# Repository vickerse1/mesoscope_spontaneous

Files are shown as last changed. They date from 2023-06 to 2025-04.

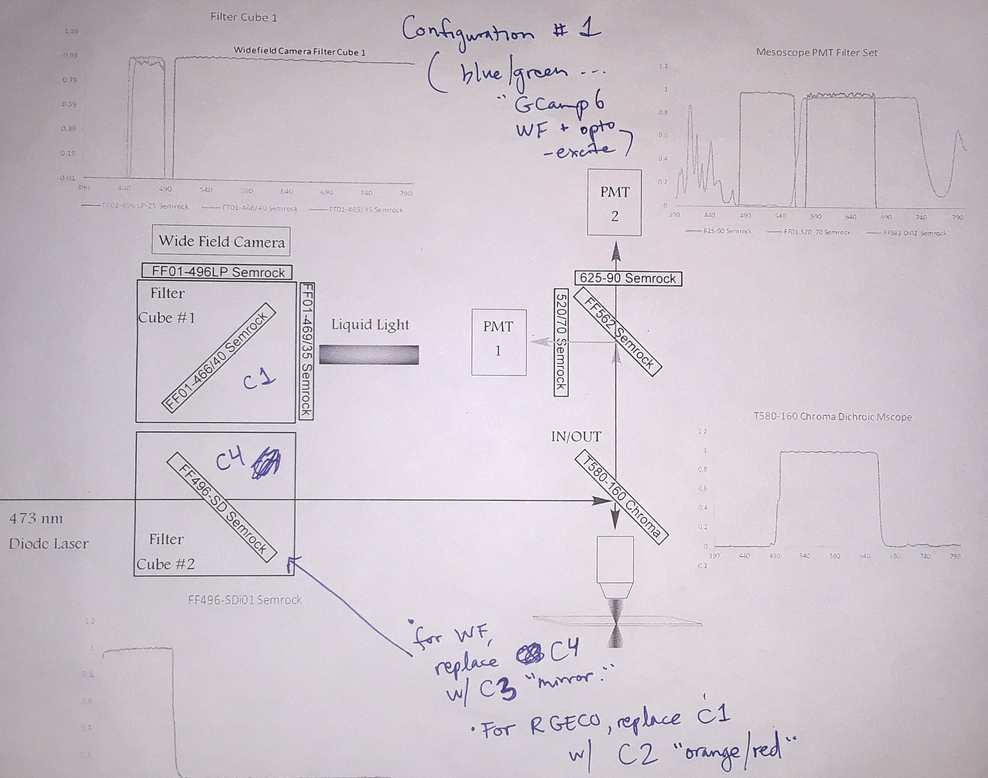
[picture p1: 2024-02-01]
mesoscope_filterCube_schematic_dual_opto_Jan0320.jpg

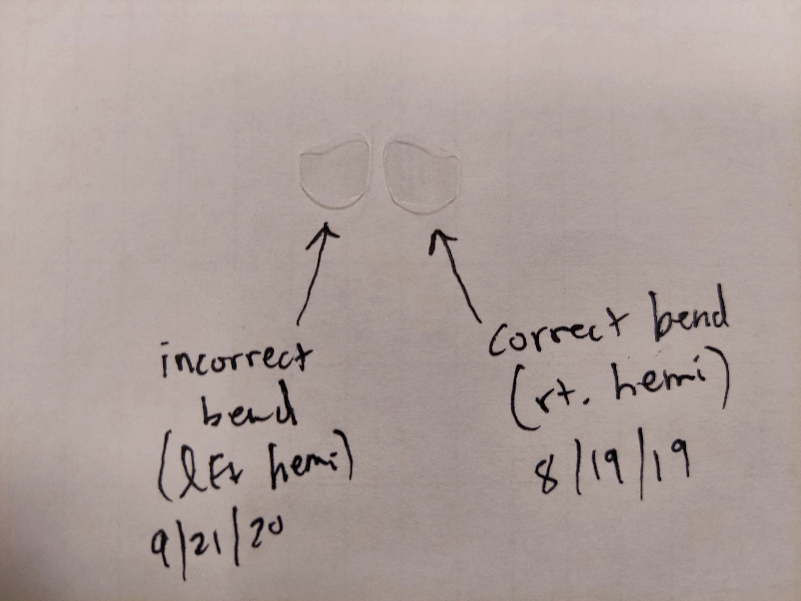
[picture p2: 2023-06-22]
cranial_windows/side_mount/side_mount_chirality_image_1.jpg

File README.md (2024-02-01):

# mesoscope_spontaneous

These files are associated with the following paper (PLEASE CITE - now online both at bioRxiv and as a reviewed preprint at eLife):

bioRxiv:

doi: [https://doi.org/10.1101/2023.10.19.563159]

eLife reviewed preprint:

[https://doi.org/10.7554/eLife.94167]

Publicly available datasets at FigShare+:

[https://doi.org/10.25452/figshare.plus.c.7052513]

"Pan-cortical 2-photon mesoscopic imaging and neurobehavioral alignment in awake, behaving mice"

Evan D. Vickers1 and David A. McCormick1,2,3

1Institute of Neuroscience, Eugene, OR. 2Professor, Department of Biology. 3Director, Institute of Neuroscience

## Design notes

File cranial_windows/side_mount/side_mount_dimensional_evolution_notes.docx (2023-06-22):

Dec2018: 10.46 mm length (ML), 9.6 mm width (AP), 10 mm radius

Aug2019: 9.8 mm length (ML), 8.8 mm width (AP), 10 and 9 mm radius (50pc/50pc)

Jul18 2020: 9.6 mm length (ML), 7.97 mm width (AP)

Jul20 2020: 8.9 mm length (ML), 7.62 mm width (AP)

Major problems:

AP too long to fit in headpost just right of midline.

Glass comes up dorsally from surface of brain just left of midline.

Glass does not drop ventrally enough over ventral A1

Solutions:

Shorten AP dimension.

Shorten ML dimension.

Decrease bend radius from 10 to 9 mm.

Concerns with new smaller glass designs: too small at AM edge to get all of M2, too small at PM edge to get all of V1?

-e

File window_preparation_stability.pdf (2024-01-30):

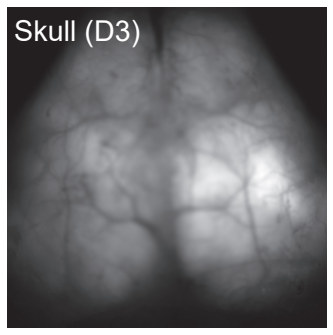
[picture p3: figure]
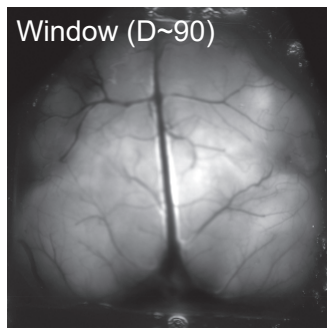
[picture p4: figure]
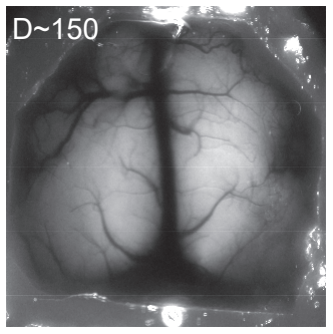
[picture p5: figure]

a | Skull (D3) | Window (D~90) | D~150

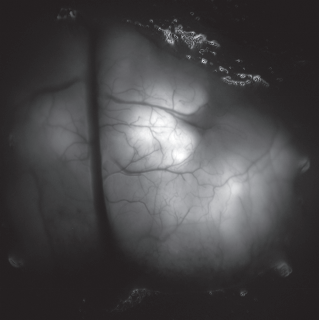
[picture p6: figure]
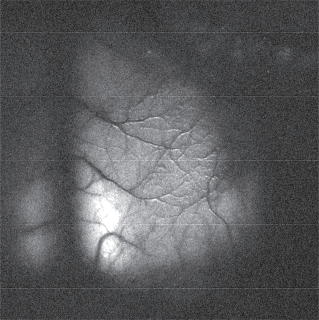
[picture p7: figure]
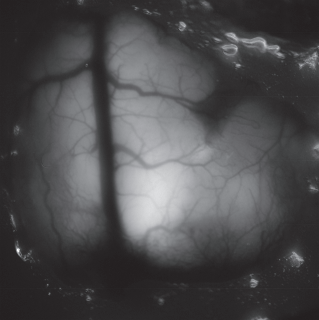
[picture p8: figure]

b

## dorsal mount

ex.

## side mount

ex.

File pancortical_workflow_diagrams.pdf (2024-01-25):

a)

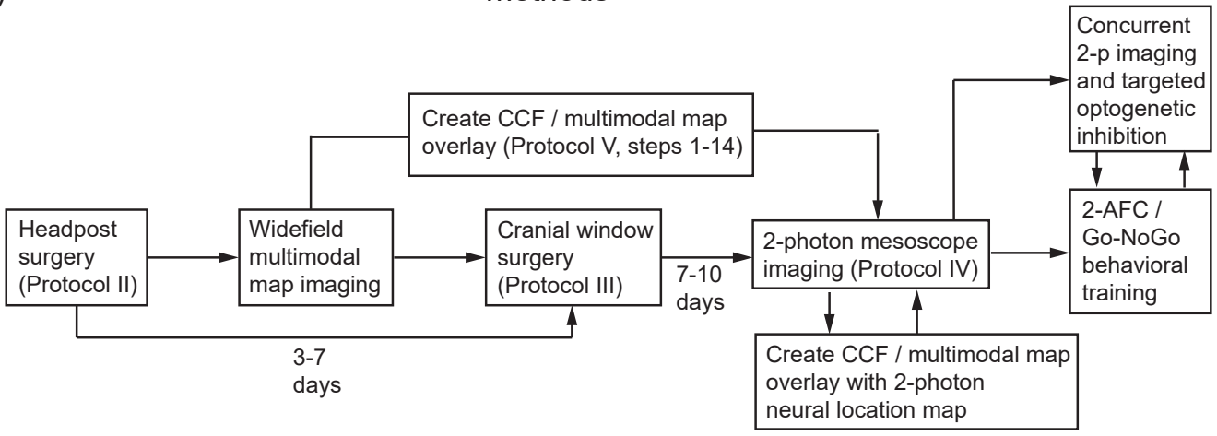
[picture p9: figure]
Headpost surgery (Protocol II); Widefield multimodal map imaging; Cranial window surgery (Protocol III); 3-7 days; 7-10 days; 2-photon mesoscope imaging (Protocol IV); Create CCF / multimodal map overlay (Protocol V, steps 1-14); Create CCF / multimodal map overlay with 2-photon neural location map; Concurrent 2-p imaging and targeted optogenetic inhibition; 2-AFC / Go-NoGo behavioral training

b)

d)

## methods

## widefield data acquisition

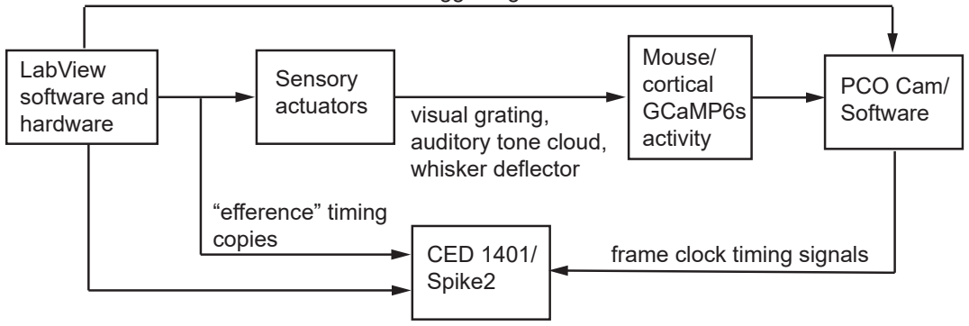
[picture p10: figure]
Sensory actuators; LabView software and hardware; CED 1401/ Spike2; PCO Cam/ Software; Mouse/ cortical GCaMP6s activity; visual grating, auditory tone cloud, whisker deflector; “efference” timing copies; frame clock timing signals
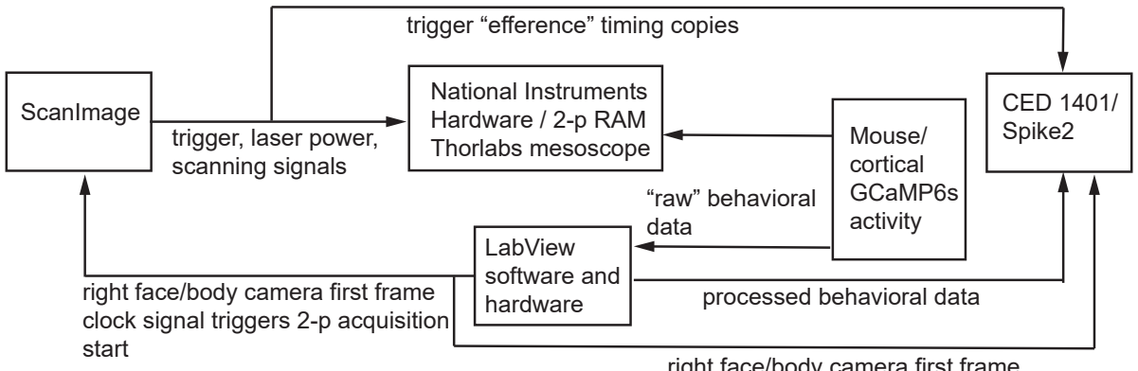
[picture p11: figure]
ScanImage; National Instruments Hardware / 2-p RAM Thorlabs mesoscope; CED 1401/ Spike2; LabView software and hardware; Mouse/ cortical GCaMP6s activity; trigger “efference” timing copies; trigger, laser power, scanning signals; right face/body camera first frame clock signal triggers 2-p acquisition start; processed behavioral data; “raw” behavioral data

## analysis

## c) 2-photon data acquisition

trigger signals

right face/body camera first frame clock signal triggers Spike2 start

Multimodal mapping/
CCF alignment
(Matlab)

Suite2p analysis
(Python)

Jupyter notebooks
mesoscope “preprocessing”
(Python)

Post-processing:
community structures
and functional connectivity (Python)

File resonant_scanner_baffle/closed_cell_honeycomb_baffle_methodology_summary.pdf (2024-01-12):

## SUMMARY OF THE INVENTION

To study the neuronal networks in behaving animals, the University of Oregon Institute of Neuroscience (ION) acquired a Thorlabs 2-photon mesoscope. This mesoscope allows for the recording of activity of over 10,000 neurons simultaneously at single-cell resolution with an acquisition rate of ~3 Hz over much of one hemisphere of the cerebral cortex of a mouse while they perform complex tasks in real-time. These tasks can involve seeing, hearing, smelling, movement, etc., even in a virtual environment.

During the auditory tests, the inventors detected unwanted high-frequency noise from the mesoscope. This noise is also detected by the mice performing auditory tasks and interferes with the data collection task being performed. Using a microphone and an oscilloscope, the inventors discovered the source of the noise to be the resonant scanners and the tubes that connect the light paths.

The inventors discovered a solution to reduce the noise level of the high-frequency sound, making use of 3D-Printers and software that enable complex designing and manufacturing of devices for optimizing scientific instrumentations. The inventors 3D-Scanned and designed a baffle having both solid and closed-cell honeycomb lattice. After installing the baffle, the high-frequency (12.5 kHz) noise went from 60 dB without the baffle down to an average of 10 dB with the baffle installed. The mice are not able to hear the high-frequency sound if the noise is below 16 dB at this sound frequency, based on published, species-specific auditory brainstem response threshold curves. Therefore, adding the baffle resulted in the mice not being able to hear the sound and also made a significant improvement in the data collection for both generic experiments where the mouse is awake and will experience stress as a result of the sound, and auditory-task-based research where precise control over the auditory environment is critical.

The sound pressure level was measured with a Bruel and Kjaer 4938 1/4" pressure-field microphone (see attached) calibrated with a Bruel and Kjaer Type 4231 Sound Calibrator, with the microphone signal amplified through a Bruel and Kjaer 1708 sound conditioner.

The sound measurements were recorded in fast fourier transform mode (FFT) on a Tektronix TDS 1002 oscilloscope. Each division on the oscilloscope display corresponded to an explicit, calibrated sound pressure level increment in decibels (dB). The output from the sound conditioner to the oscilloscope was sent by BNC cable.

A Creaform HandyScan Black Elite 3D-Scanner was used to create a digital CAD of the existing setup of the Thorlabs Mesoscope. Live capture of the scan data was performed using VX Elements software and the same software was used to convert the live scan to a CAD file of .STL (stereolithography) file format. Using the scanned CAD as a reference, the team designed a baffle to custom fit onto the mesoscope resonant scanner and tubes using Autodesk Fusion-360 software. After designing the baffles, the CAD file of the designed baffle was imported into Materialise Magics software and the lattice design having solid walls followed by honeycomb latticing was designed using this software. The latticed files were saved in .STL file format. In addition, using Materialise Magics, a manual fixing operation was done on certain regions of the imported CAD which had unwanted noise shells, planar holes, overlapping triangles – all of which were fixed to ensure a high quality CAD file is produced for 3D-Printing.

The final baffle design included mediums of varying densities from solid walls and honeycomb latticing to 3D-Print in Nylon. The baffle was printed using Powder Bed Fusion technology using Formlabs Fuse machine, where Nylon material is sintered layer-by-layer to create a 3D-object. The design intent of the honeycomb lattice was to allow for nylon material to be enclosed inside the closed cells during the printing process. The inventors added a clearance design between the baffle and the resonant scanning components to allow for the fitment of polyurethane foam. This created a baffle where high-frequency sound waves had to penetrate through foam, solid nylon wall, enclosed nylon powder inside the honeycomb followed by a second solid wall.

The adhesive back foam used for the baffle was Polyurethane foam 1/8 inches thick and medium soft with 3/16 inch extra soft foam. The foam was cut to shape using a laser cutter to adhere to the 3D-Printed components. High-frequency noise data were collected with a microphone and an oscilloscope. The microphone was fixtured in the general area of the location where the mice would perform auditory tasks.

The baffle is a first-of-its-kind attachment to the Thorlabs Mesoscope (US Pats. 10901194 and 10295811, incorporated herein by reference) and is not commercially available. Since 3D printing allows for mass customization, this baffle can be adapted for any resonant scanning microscopes on the market. This will reduce unwanted noise levels from the experiments yielding to better experimental results for auditory research and also allow for a safer environment for users since the high-frequency noise can be detected by researchers and users of such devices.

The target goal was to lower the noise level to below 16 dB when performing auditory tasks on mice. The results indicate that the 12.5 kHz noise went from 60 dB without the baffle down to an average of 10 dB with the baffle installed.

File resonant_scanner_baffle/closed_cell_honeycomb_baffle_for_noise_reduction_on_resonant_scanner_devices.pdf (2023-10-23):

Closed-cell honeycomb baffle for high-frequency noise reduction on Resonant Scanning devices

Supplementary Document

3D-Scanning

The 3D-Scanning is performed to ensure a) an accurate digital representation of the setup is captured for reverse engineering a custom-fit baffle around the components. b) to perform a virtual fitment check to ensure the designed baffle fits the existing components.

The software used to capture scanned point cloud data is Creaform VX Elements and the file is aligned to coordinate planes using Materialise Magics.

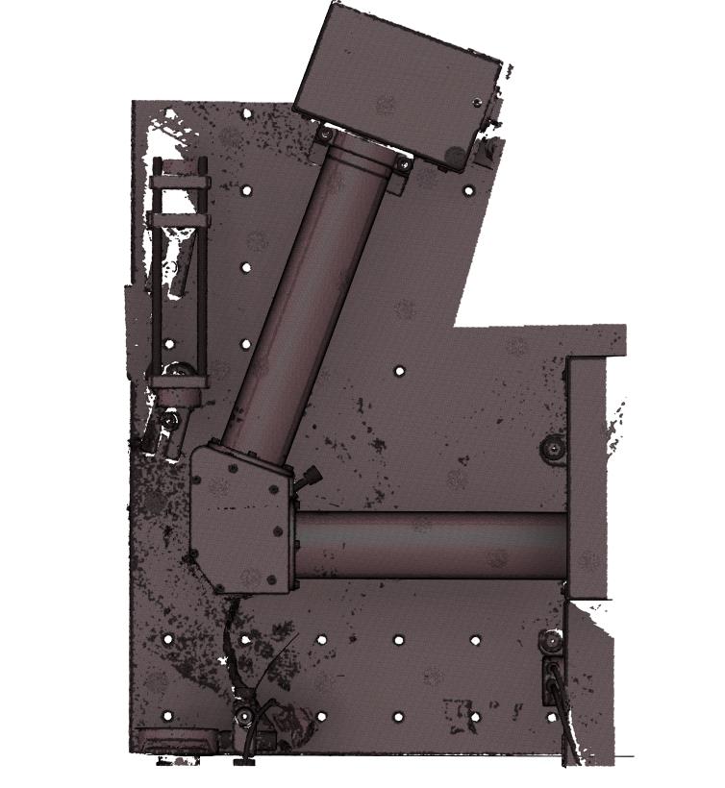
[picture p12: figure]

Reverse Engineering

Using the 3D-scan file, a custom baffle enclosure is designed using Autodesk Fusion-360. The components are designed to be produced in seven individual pieces for a) easy disassembling for technicians and b) constraints set forth by the limited printable build area by the 3D-Printer. This design consisted of solid walls that will be later used to create latticing on the inside and also contains an offset for an after-market polyurethane foam to compress. The design has custom screws and plugs for adjustment of a calibration screw fitted in the resonant tubes.

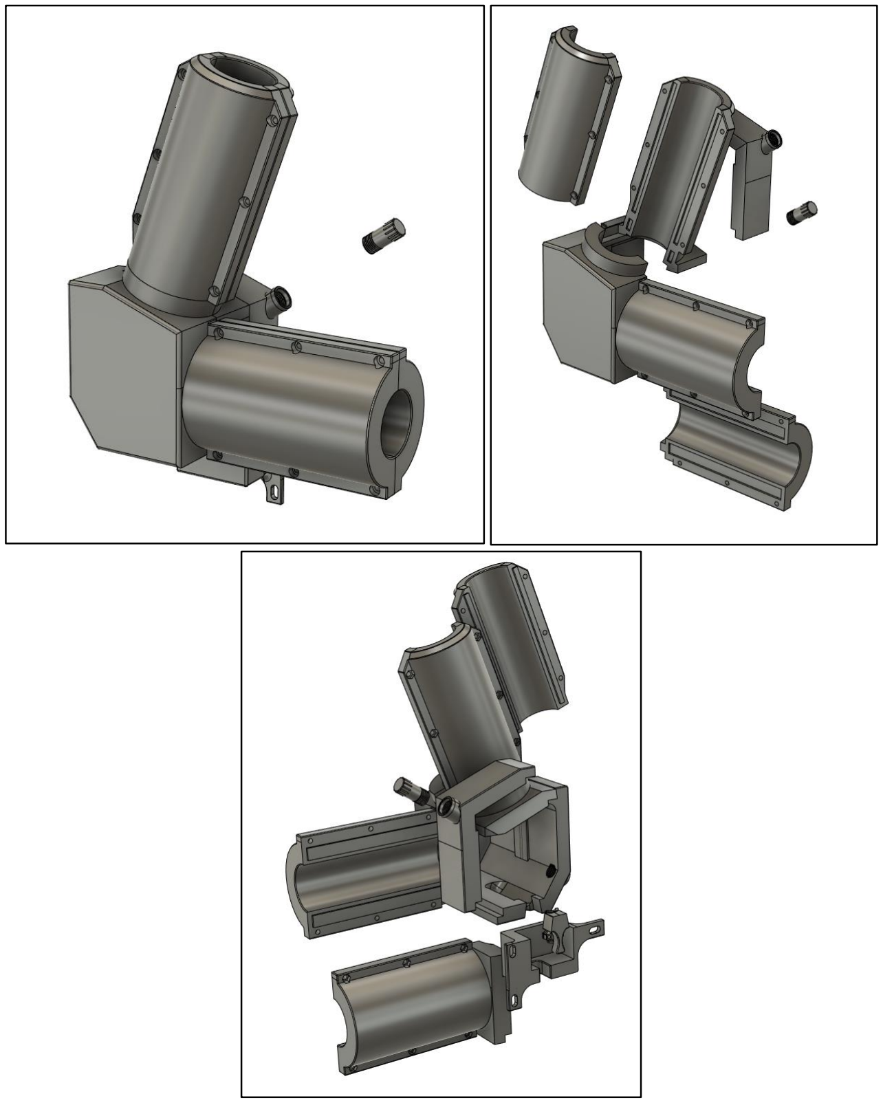
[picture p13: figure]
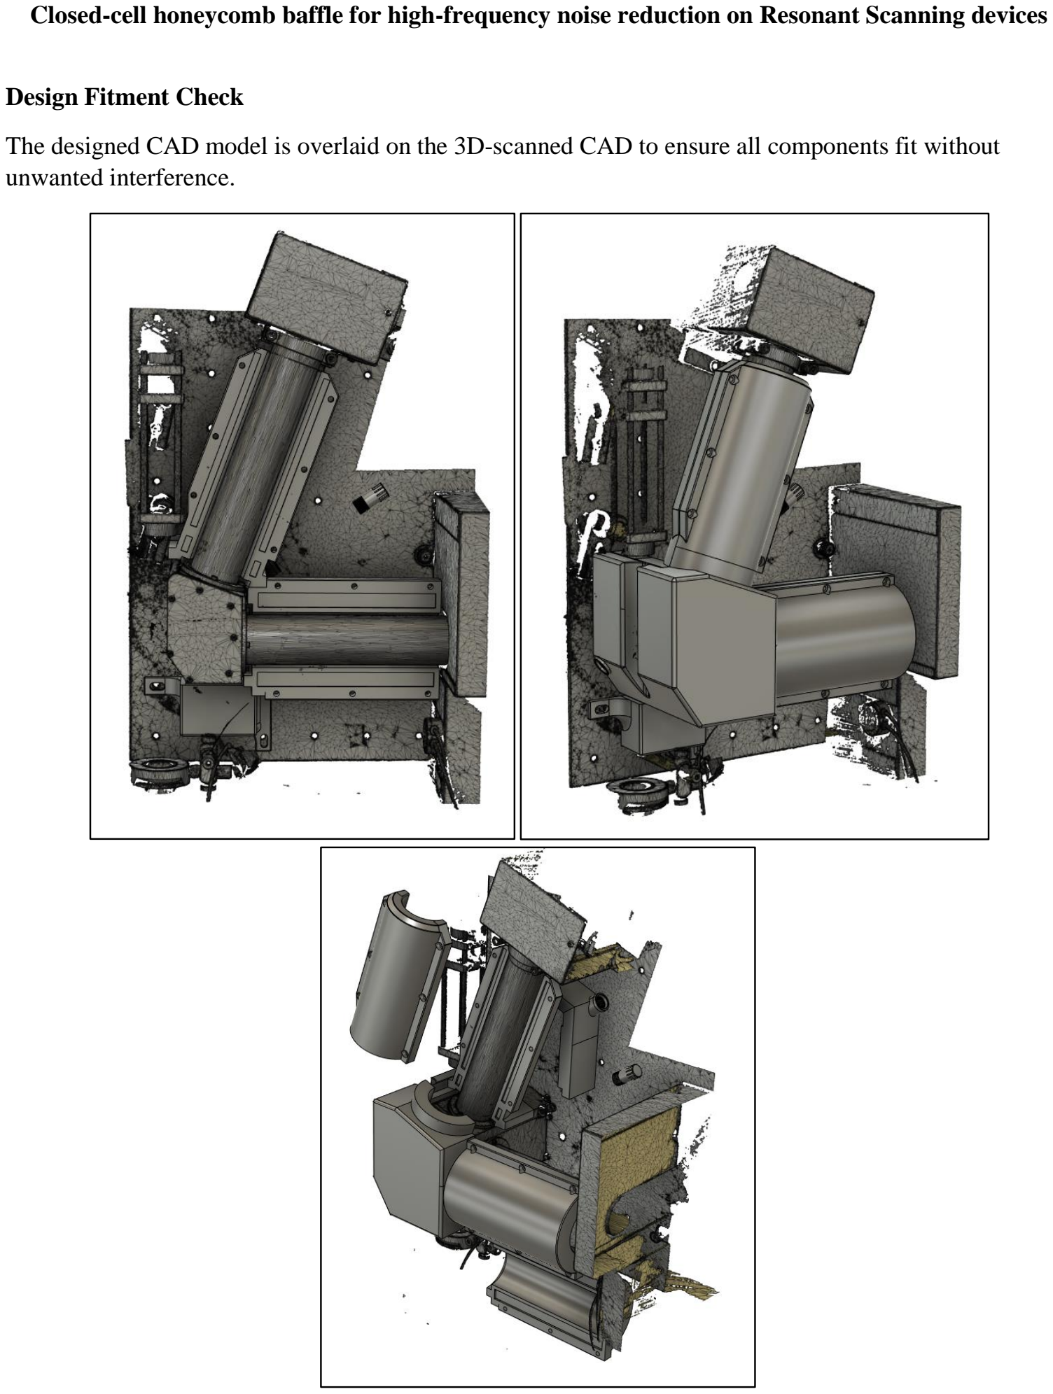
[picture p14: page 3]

Design Fitment Check

The designed CAD model is overlaid on the 3D-scanned CAD to ensure all components fit without unwanted interference.

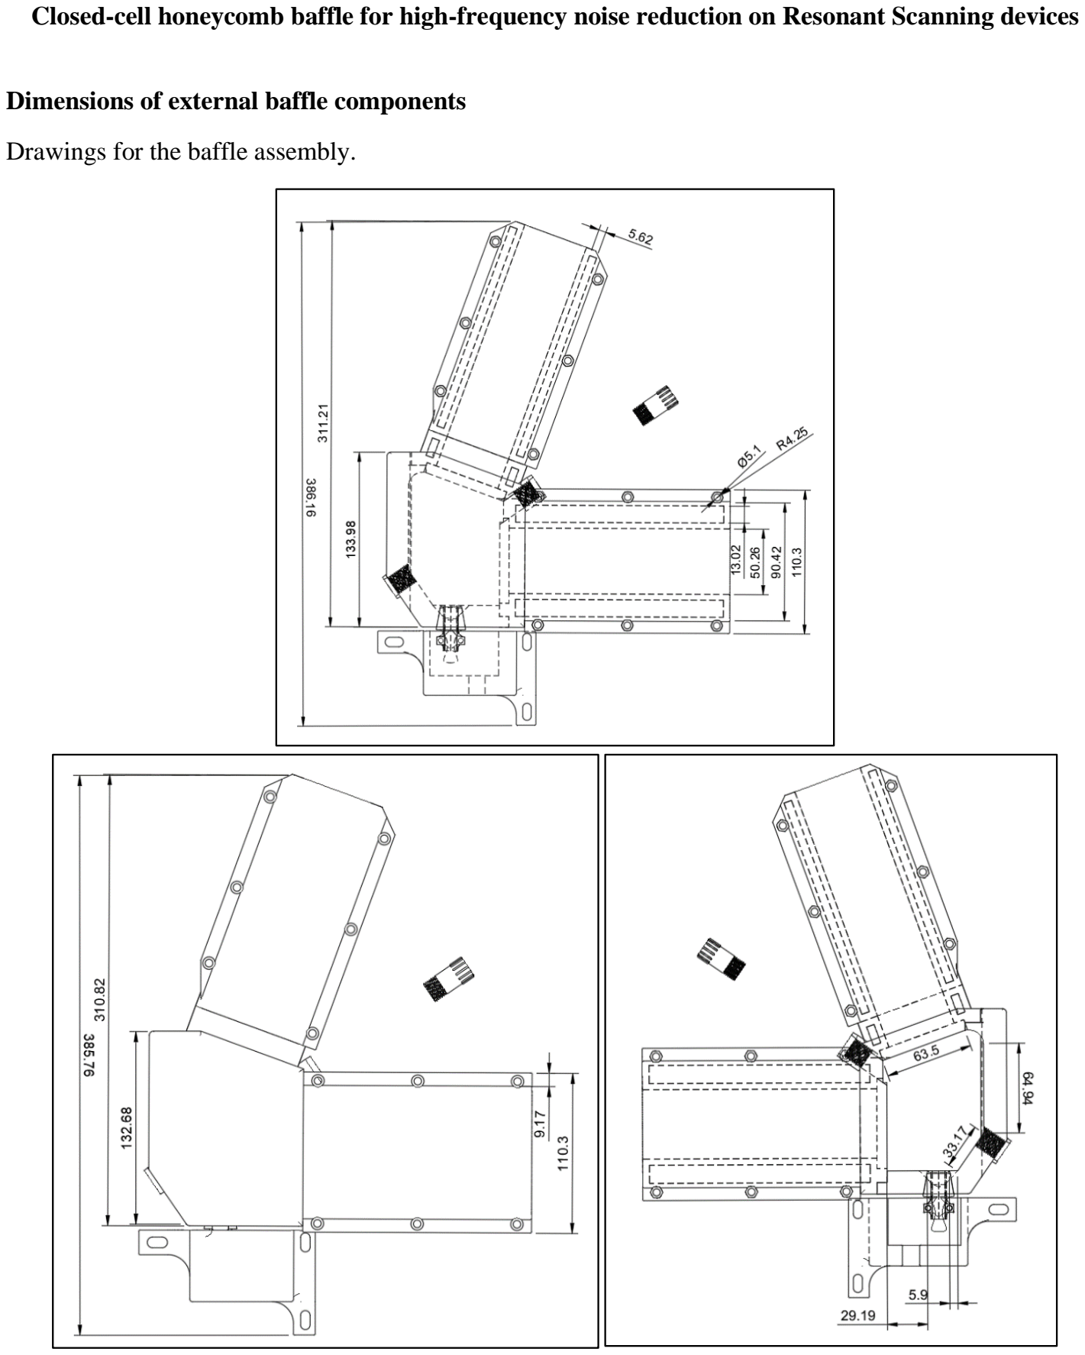
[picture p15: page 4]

Dimensions of external baffle components

Drawings for the baffle assembly.

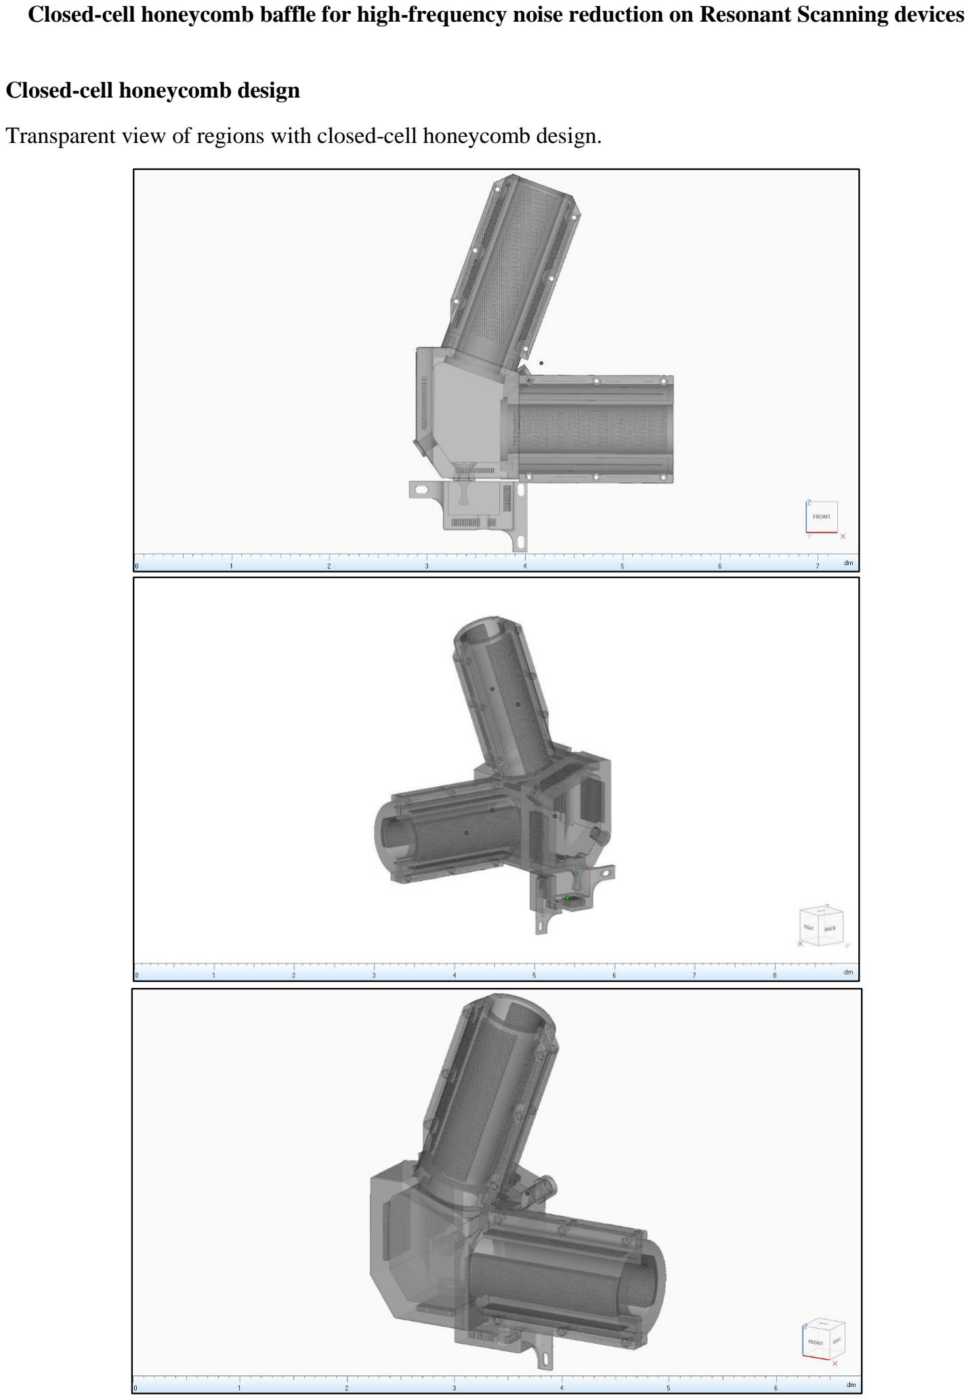
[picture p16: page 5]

Closed-cell honeycomb design

Transparent view of regions with closed-cell honeycomb design.

Dimensions of closed cell honeycomb design

Annotated dimensions of the closed-cell honeycomb design.

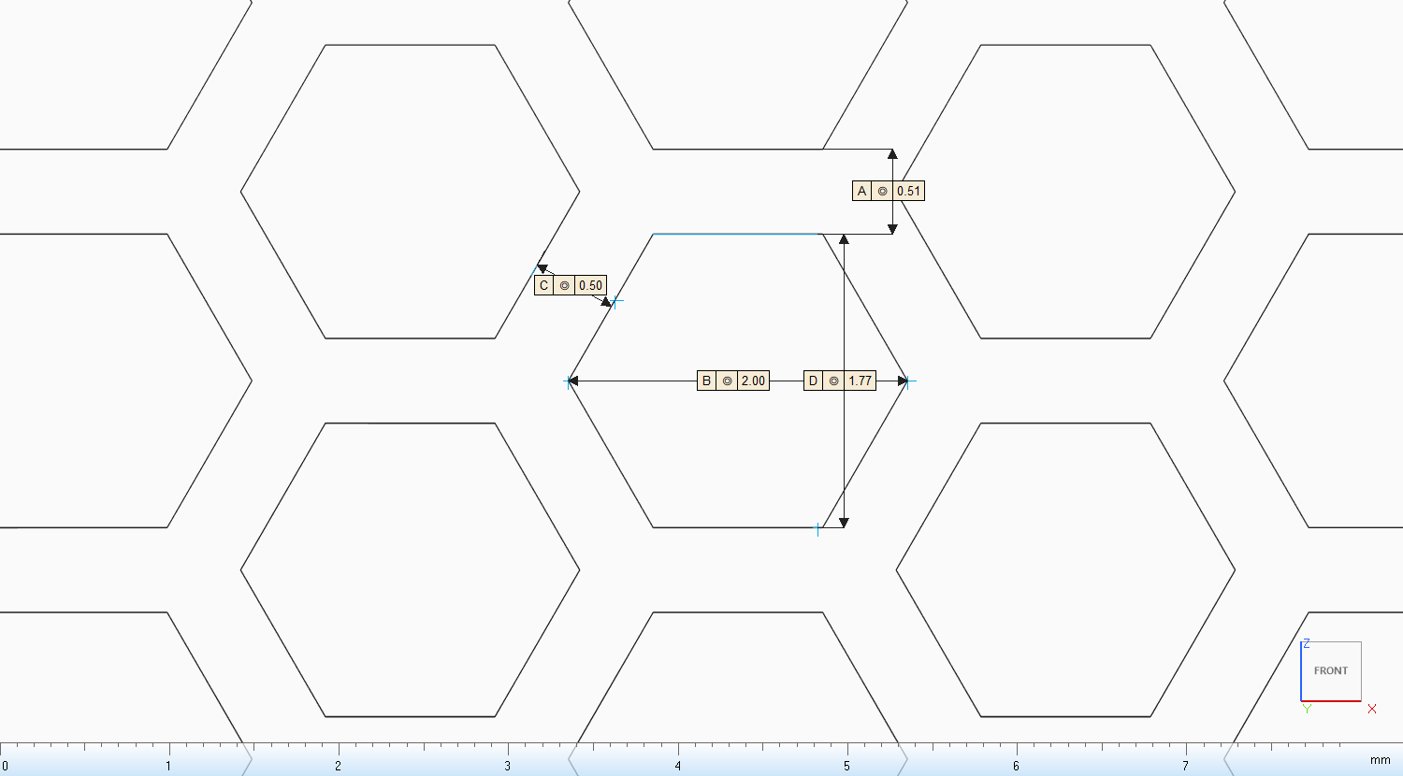
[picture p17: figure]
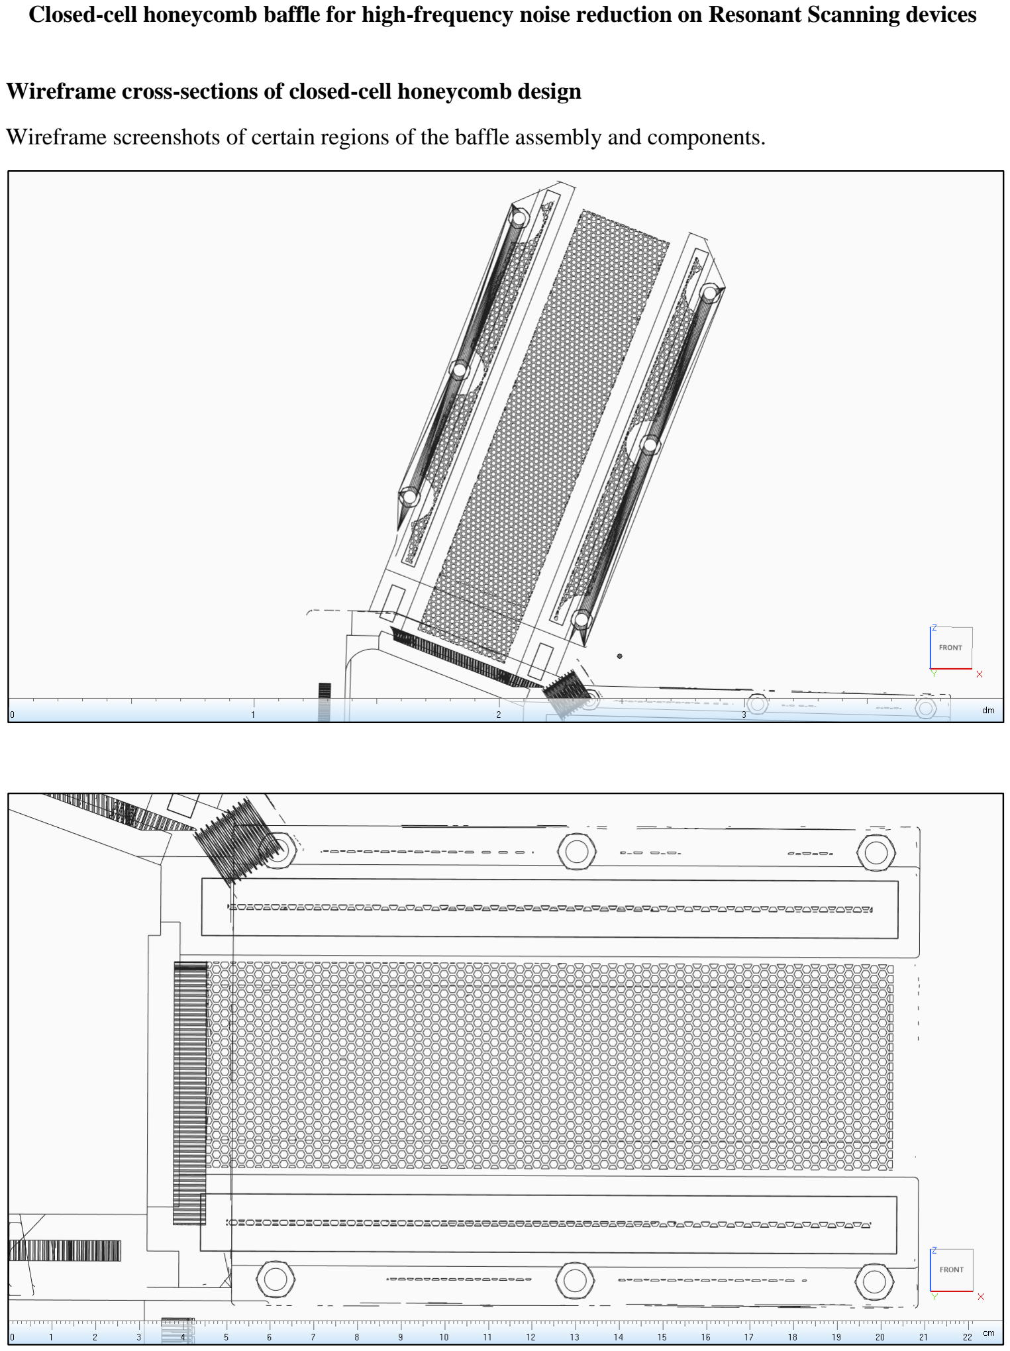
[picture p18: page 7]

Wireframe cross-sections of closed-cell honeycomb design

Wireframe screenshots of certain regions of the baffle assembly and components.

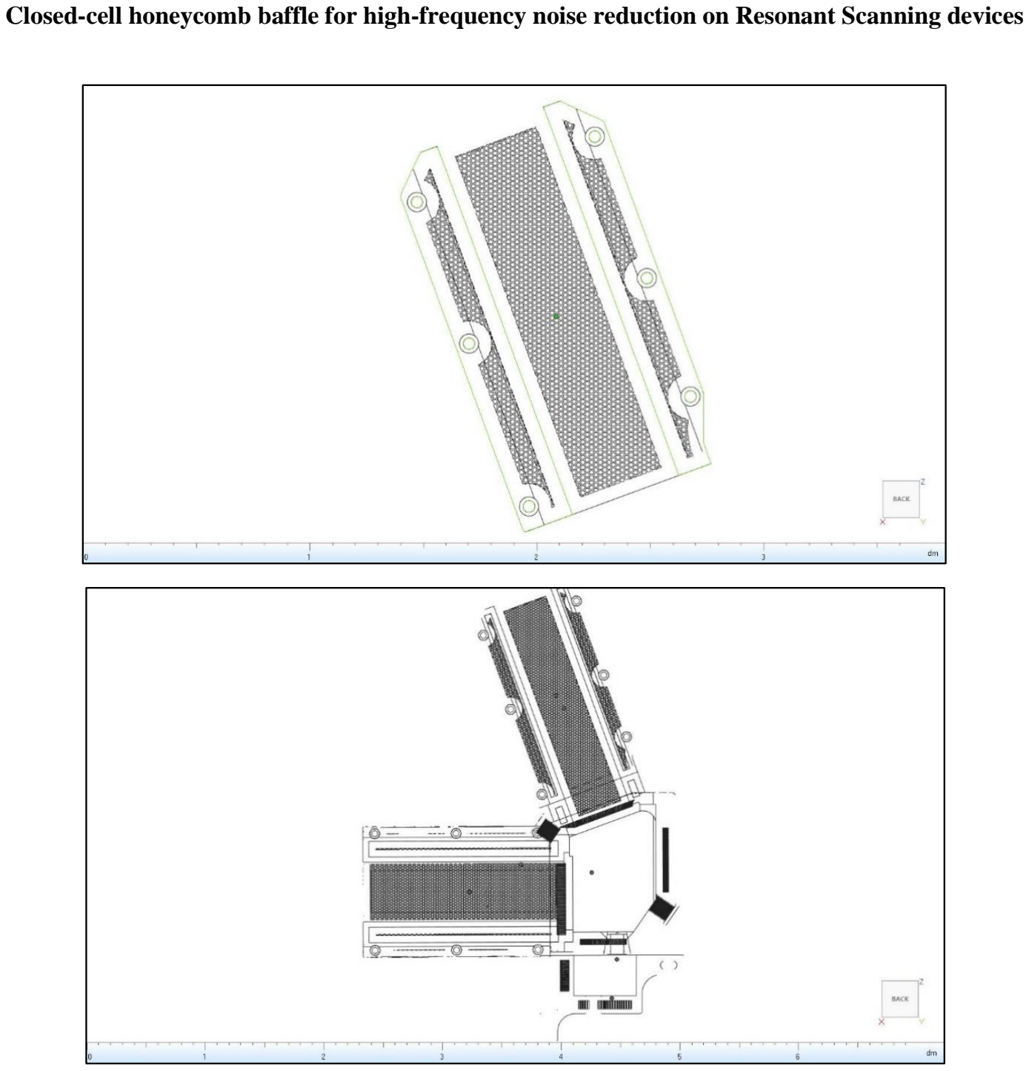
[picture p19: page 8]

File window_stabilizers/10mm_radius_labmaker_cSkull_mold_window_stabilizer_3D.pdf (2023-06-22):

setPageBoxes("Crop", 0, 0, [0,2000,2000,0]);

TITLE PART NO | 10mm_radius_labmaker_cSkull_mold_window_stabilizer_Apr0119 REVISION DESIGNER | McCormick Lab ENGINEER NOTES

THE INFORMATION AND/OR MATERIAL IN THIS DOCUMENT IS THE PROPERTY OF AND RESTRICTED INFORMATION AND/OR MATERIAL OF THE AUTHOR. THIS INFORMATION MAY NOT BE USED, REPRODUCED, PUBLISHED OR DISCLOSED TO OTHERS WITHOUT WRITTEN AUTHORIZATION. IT IS TO BE USED ONLY FOR MANUFACTURING ITEMS SPECIFIED WITHIN THE DOCUMENT.

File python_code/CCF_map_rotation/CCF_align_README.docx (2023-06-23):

Install UOBRAINFLEX python env from sjara github page

Min python 3.7.2 (3.8.5 also works), matplotlib 3.1.3 or 3.3.2, skimage 0.19.1

Need to update matplotlibrc.template file from github?

Open spyder 4.15 or newer from inside anaconda browser after selecting uobrainflex environment while in “home”

Select wrench icon at top in spyder, set python interpreter as envs/uobrainflex/python.exe

Select ipython console/graphics and set graphics backend to by Qt5

Run Rotate_CCF.py to create areas, CCF, masks, and outlines.npy files in folder named after rotation degree (22deg for A1V1M2 – thus positive is view angle rotated right to look at rt ctx)

Run ccf_alignment.py. Use output of kaufman and saxena matlab multimodal map protocol (see other instructions) as mmm and the output of rotate_ccf (see above) as the ccf. These input image files should end in “_MMM.png”.

Select one mmm pt then corresponding ccf pt, then next mmm pt then corresponding ccf pt, etc.. First four pts should be external bounding box. Select at least 5 internal pts.

The output of this step is: STD_ccf_points.npy, and STD_mmm_points.npy. These files are put in the same folder as the mmm image.

Load data in suite2p and create mean image png output in corresponding target session analysis folder (top level). Add “_MMM.png” suffix.

Next, run analyze_WF_session_meso_Feb1022.py. First image input is CCF, second image input is mmm, and third image input is target session image (can do unrotated…if pre-rotated, may need to change border threshold cutoff from 0.001 back to 0.01.

Output is masks w/o overlap corrected, masks w/ overlap corrected, and border map (also shown as figs); also output are npy files containing session_mmm and session_vessel alignment / warping points.

Can change color of each mask to indicate mean arousal correlation, arousal correlation variance, arousal correlation spatial heterogeneity factor, etc….

For each cell detected in Suite2p, get (x,y) position. Then, loop through all masks. For each mask, check to see if (x,y) position of each mask pixel matches that of cell. If yes, add region ID to cell dictionary, update arousal correlation summary stats (see above) for that mask region.

Awesome!...!

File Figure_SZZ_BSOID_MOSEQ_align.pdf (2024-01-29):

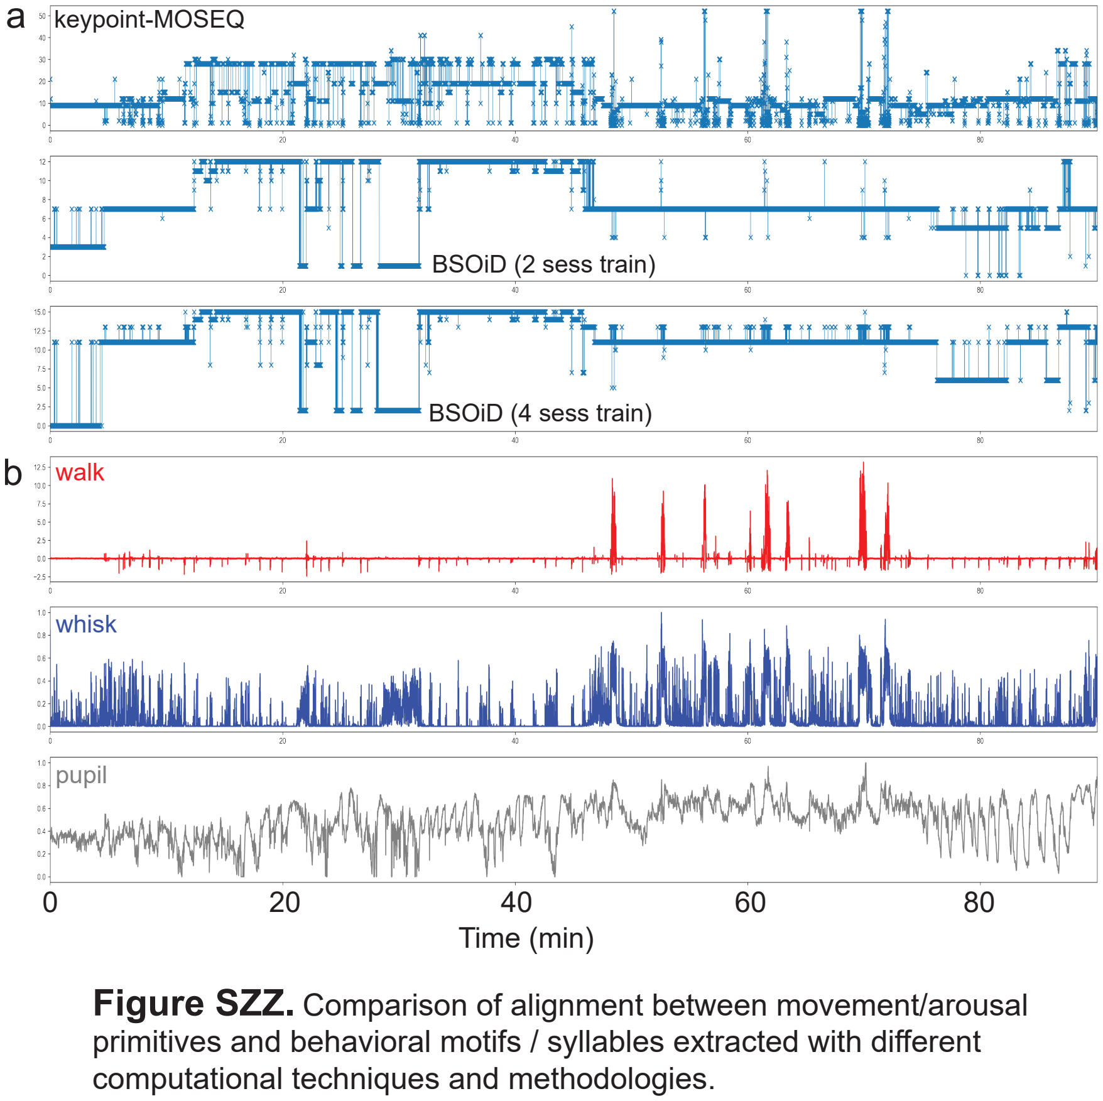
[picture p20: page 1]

keypoint-MOSEQ

BSOiD (2 sess train)

BSOiD (4 sess train)
walk

whisk

pupil

a

b

Figure SZZ. Comparison of alignment between movement/arousal primitives and behavioral motifs / syllables extracted with different computational techniques and methodologies.

Time (min)

0 | 20 | 40 | 60 | 80

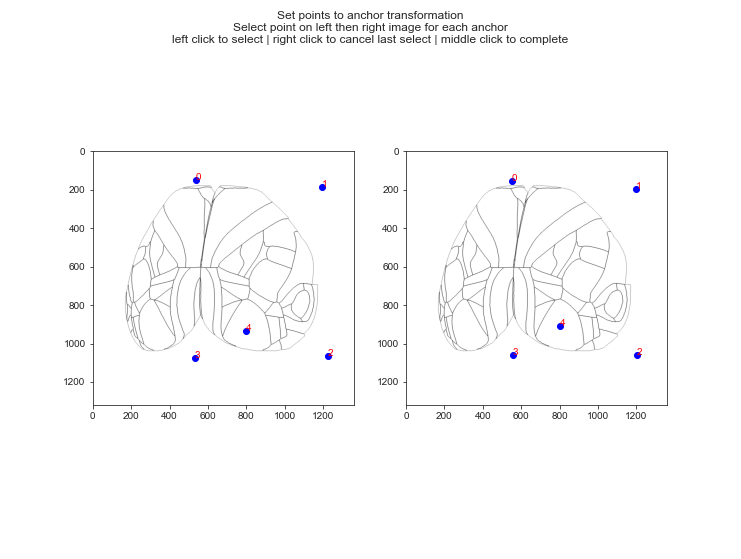
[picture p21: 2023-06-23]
python_code/CCF_map_rotation/22deg/CCF_mmm_ccf_fit.png

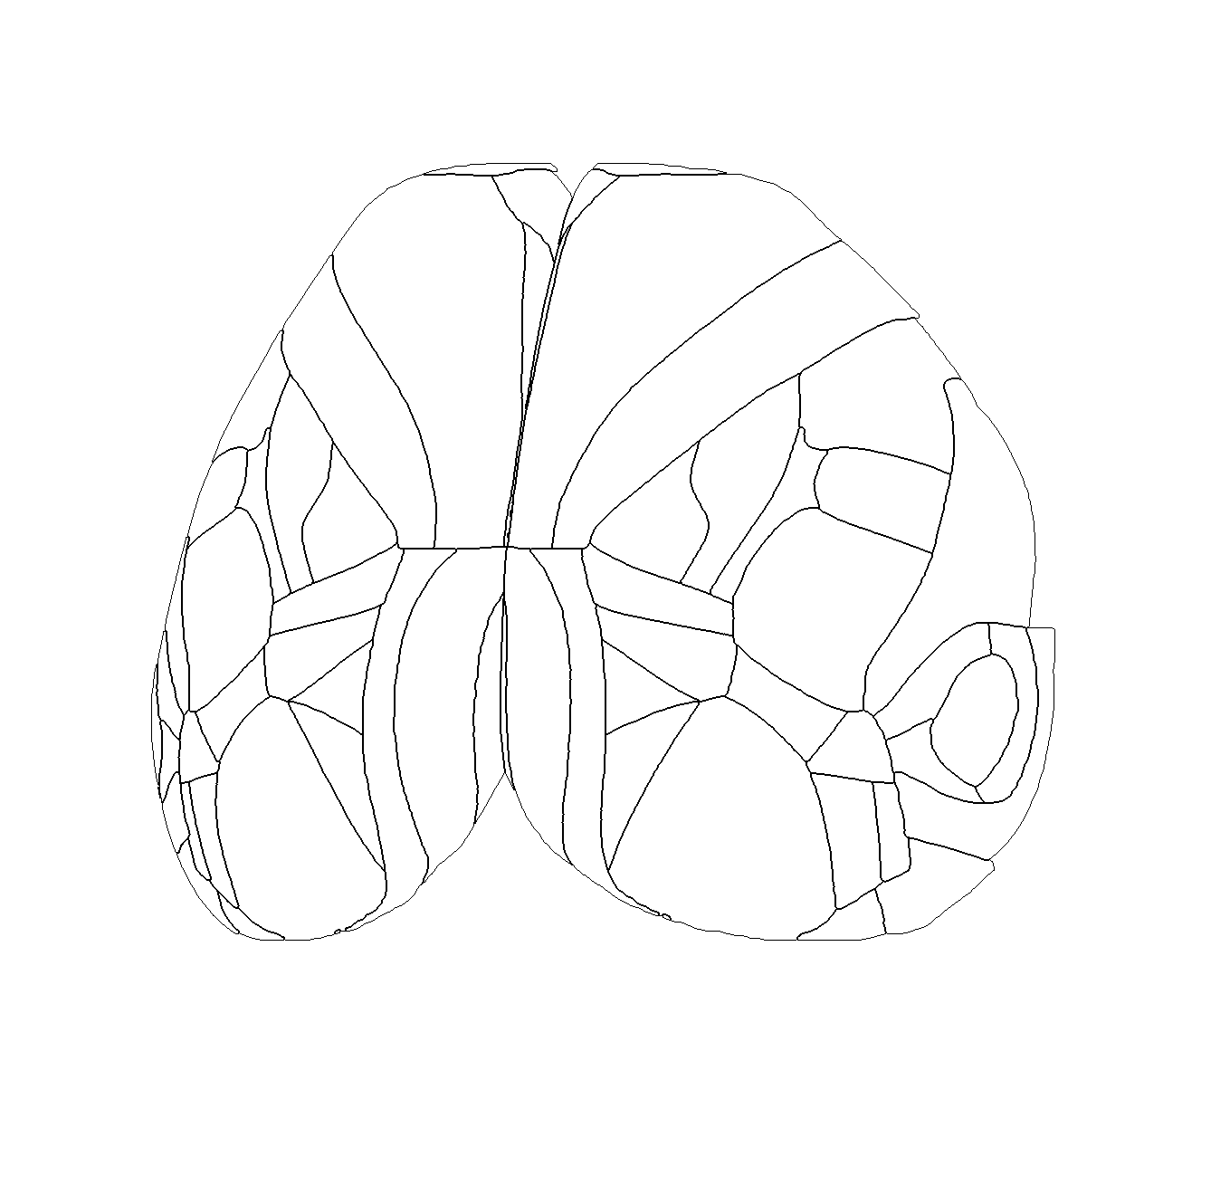
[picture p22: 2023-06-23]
python_code/CCF_map_rotation/22deg/CCF.png

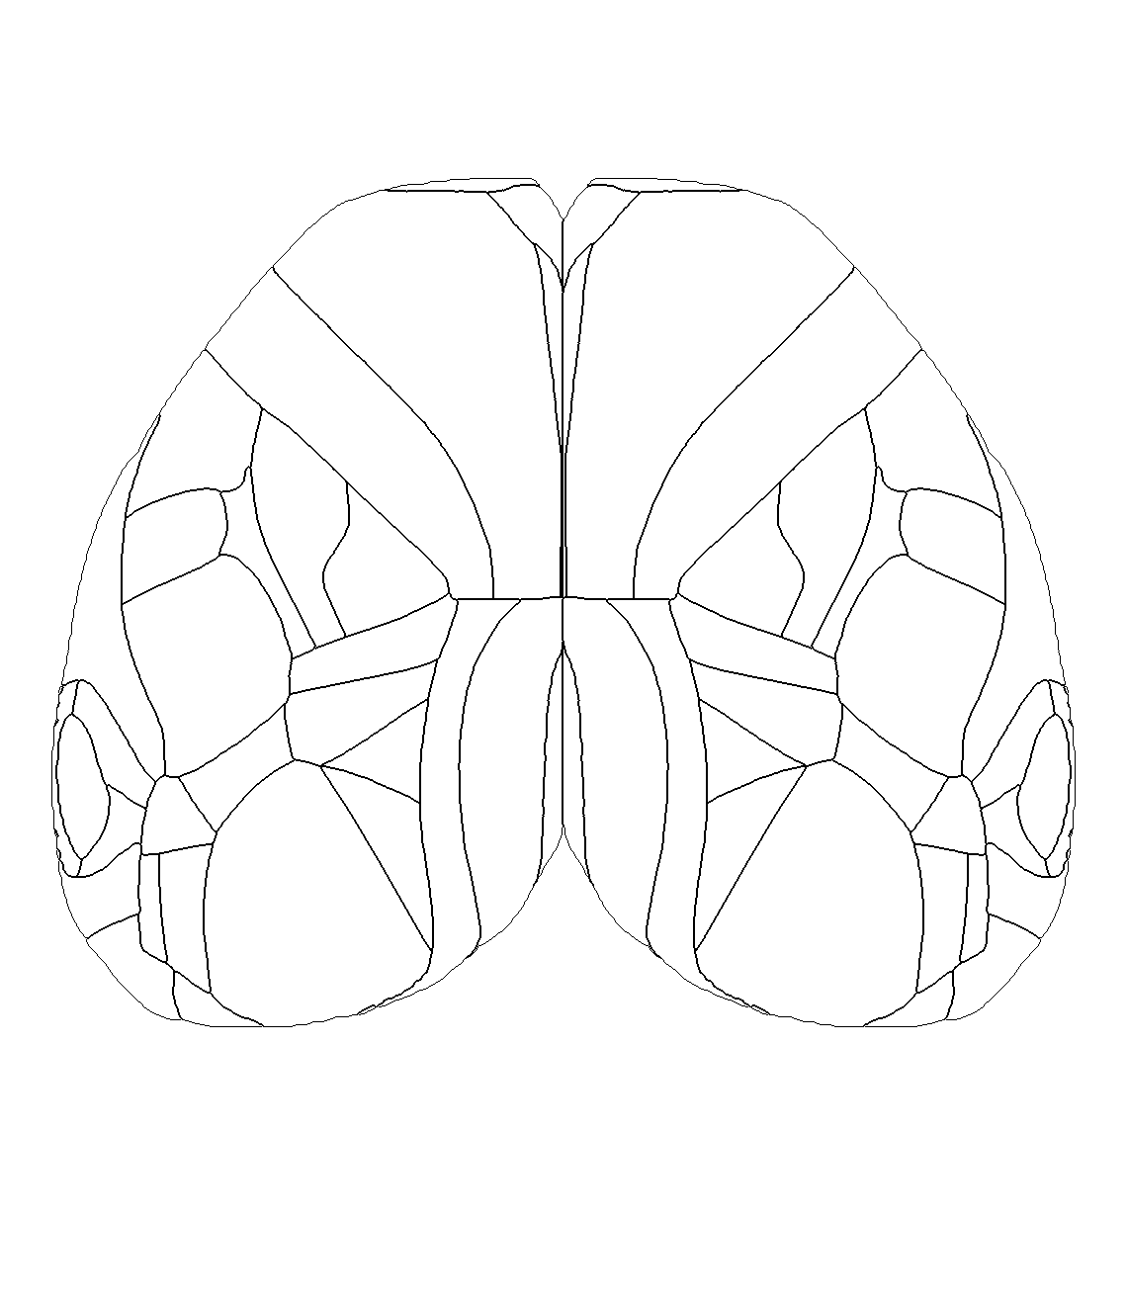
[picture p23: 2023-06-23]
python_code/CCF_map_rotation/0deg/CCF_MMM.png

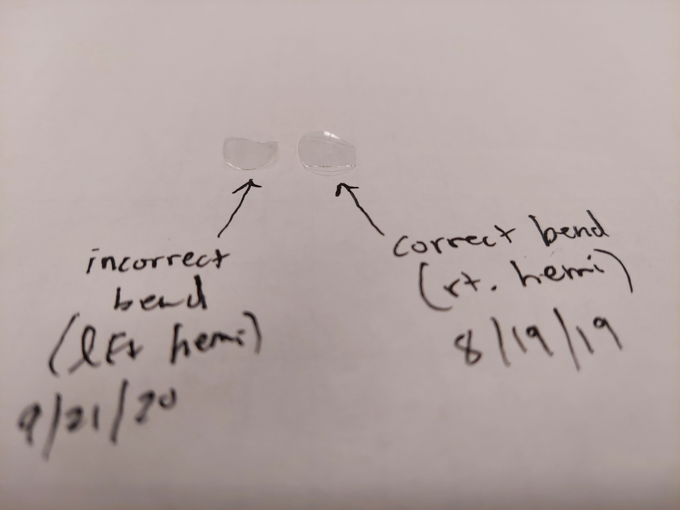
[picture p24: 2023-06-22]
cranial_windows/side_mount/side_mount_chirality_image_2.jpg

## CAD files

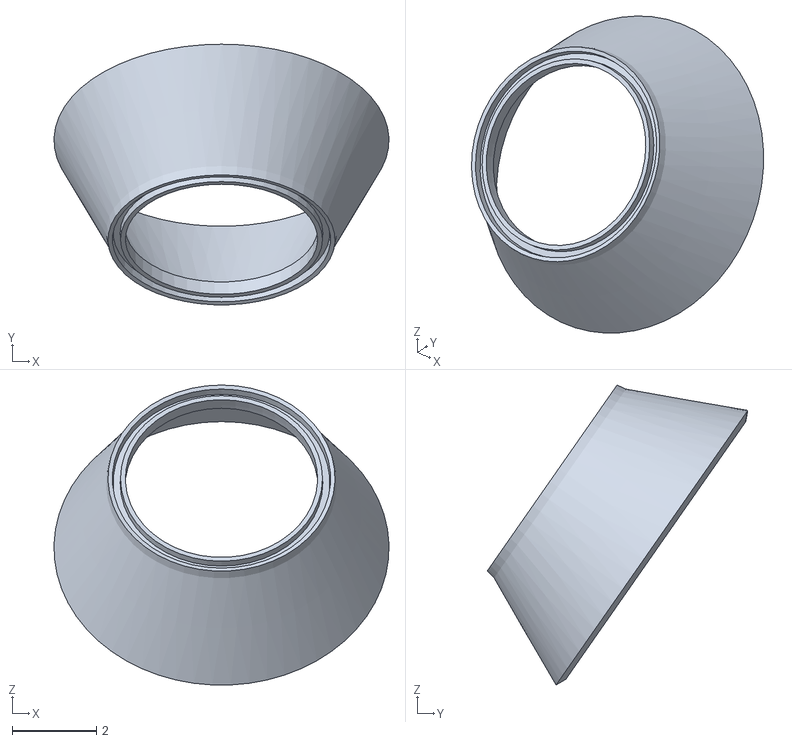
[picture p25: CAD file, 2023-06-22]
side_mount_woks/side_mount_wok2_full_alt.stl
7.96 x 6.19 x 7.13

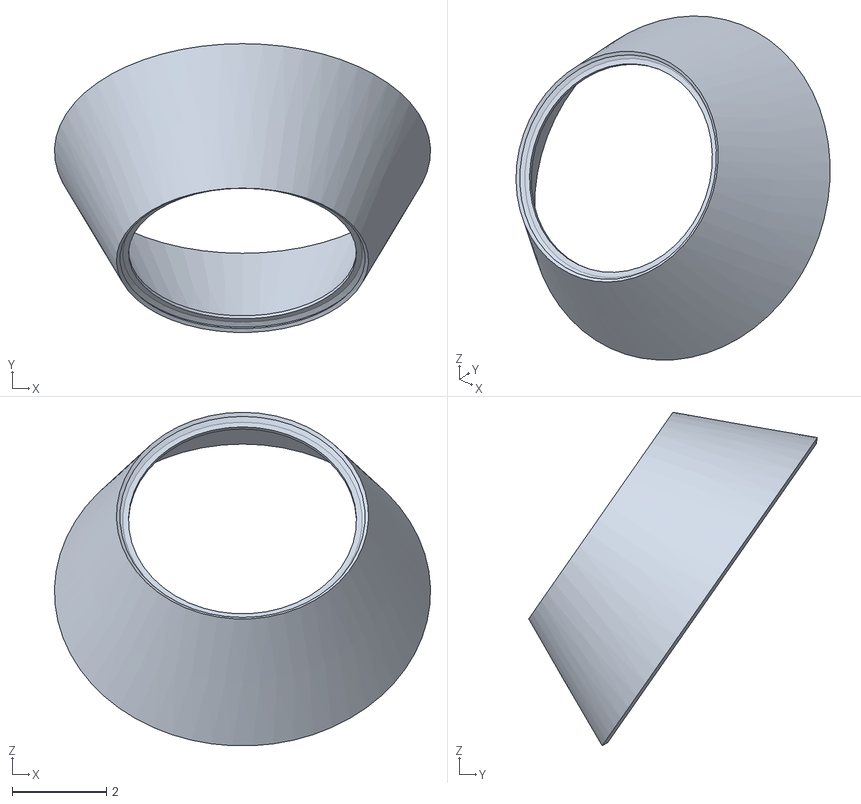
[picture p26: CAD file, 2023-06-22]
side_mount_woks/side_mount_wok2_full.stl
7.96 x 6.11 x 7.06

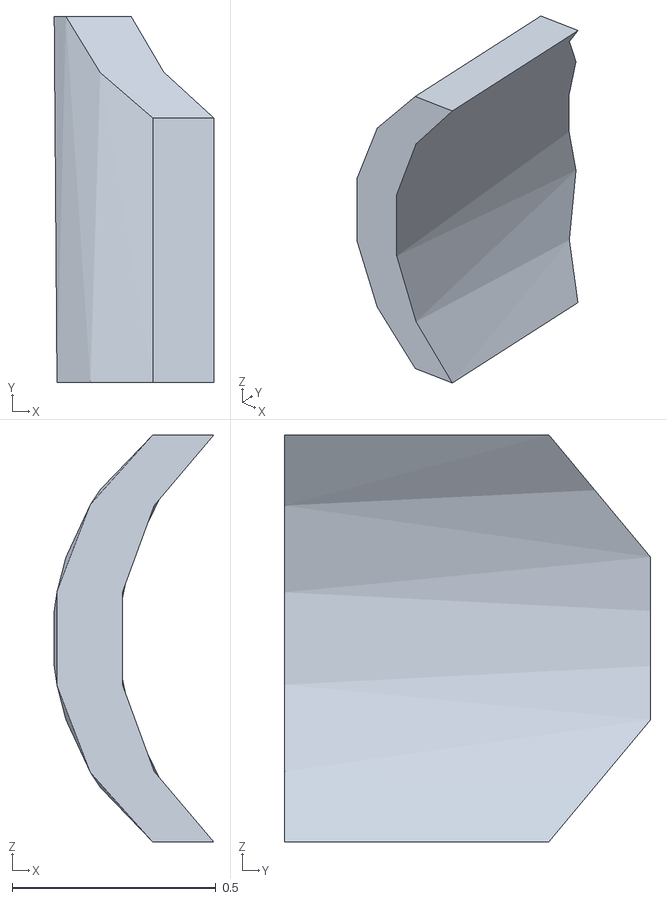
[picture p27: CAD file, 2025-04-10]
cranial_windows/dorsal_mount/13mm_radius_mold_with_crystal_skull.stl
0.392 x 0.899 x 1.00

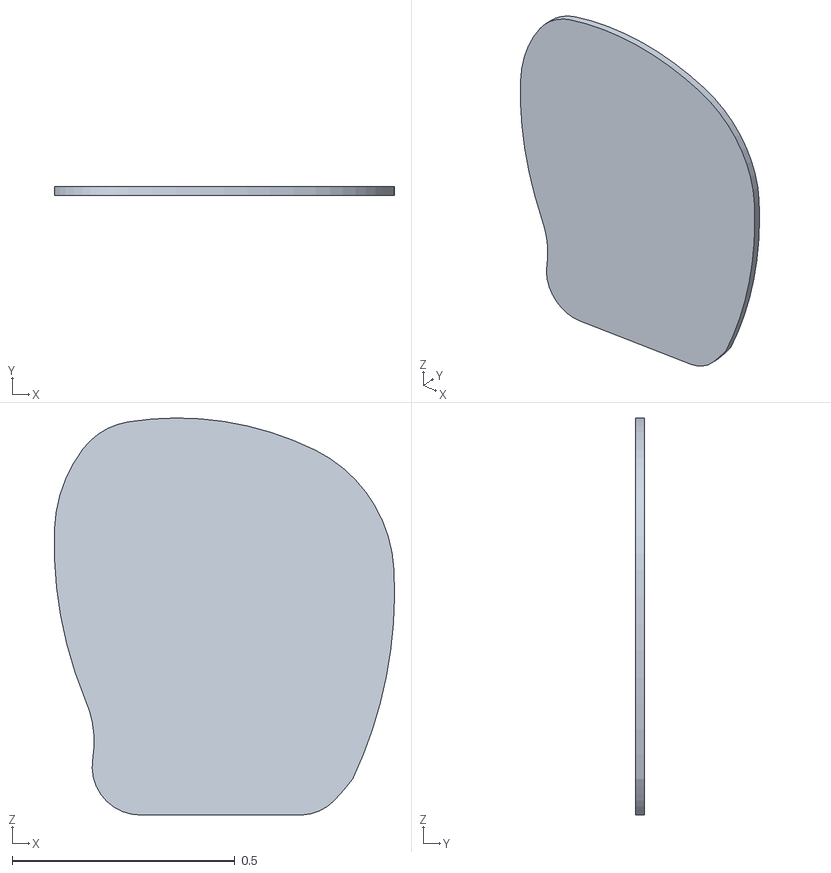
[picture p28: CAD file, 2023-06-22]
cranial_windows/side_mount/side_mount_large_10_mm_radius_3D_v2.stl
0.764 x 0.02 x 0.892

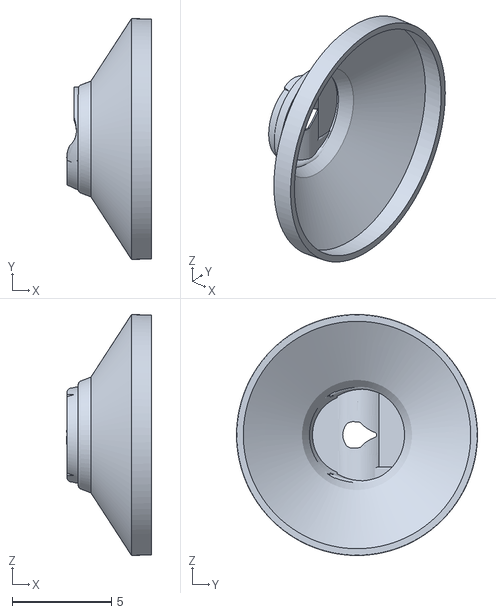
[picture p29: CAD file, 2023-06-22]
dorsal_mount_woks/dorsal_mount_widefield_combined_alt.stl
4.27 x 12.2 x 12.2

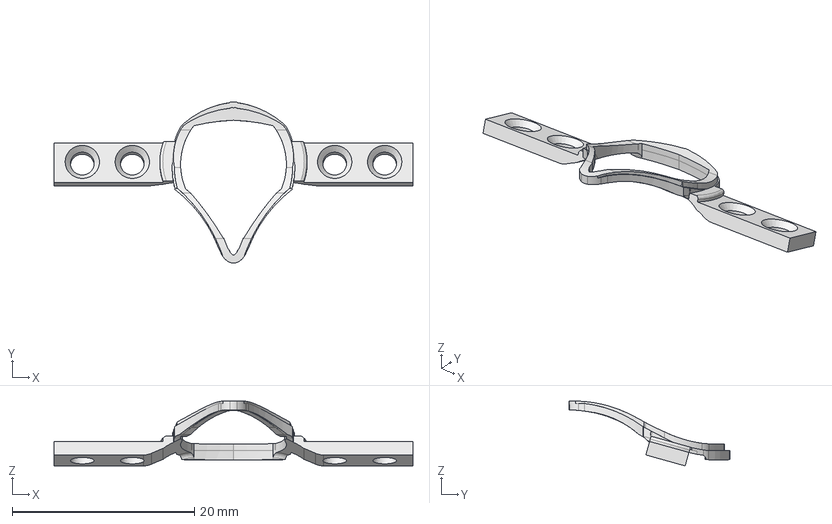
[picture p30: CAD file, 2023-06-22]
headposts/dorsal_mount/dorsal_mount_small_alt.stp
39.4 x 17.7 x 7.12 mm

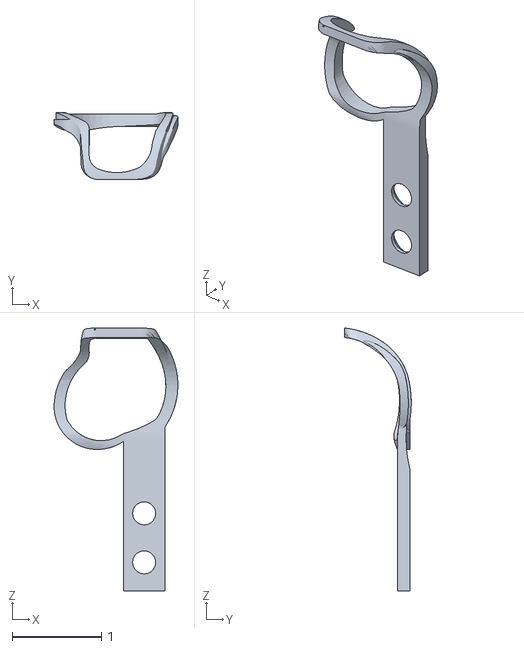
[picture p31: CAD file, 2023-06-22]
headposts/side_mount/left_cortex/side_mount_left.stl
1.39 x 0.748 x 2.95

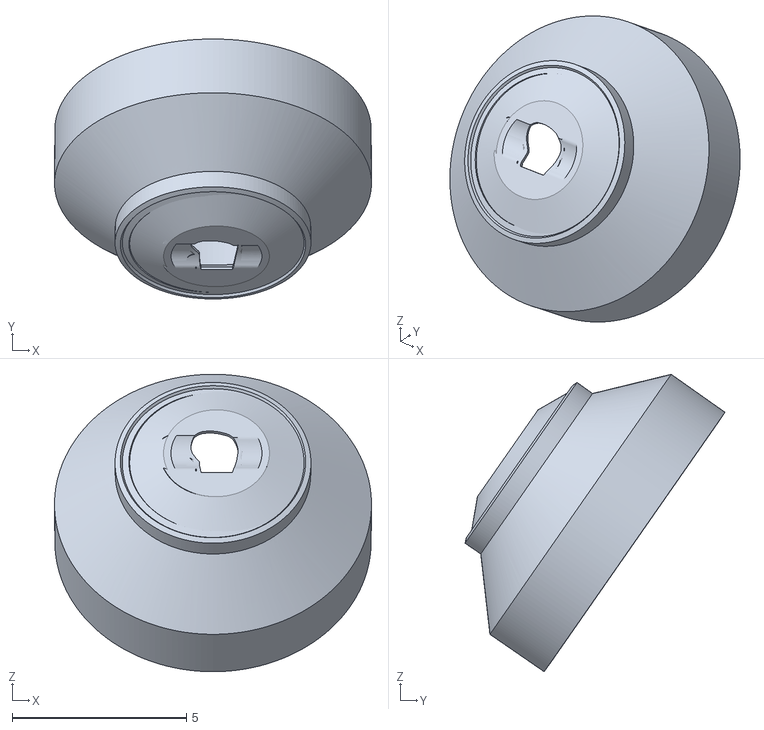
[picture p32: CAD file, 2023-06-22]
side_mount_woks/side_mount_wok1_wok2_fused.stl
9.11 x 7.47 x 8.54

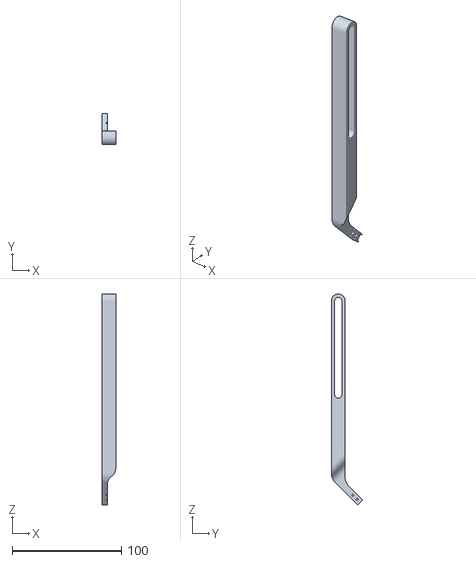
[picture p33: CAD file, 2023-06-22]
support_arms/right_support_arm.stl
12.7 x 28.7 x 193.2

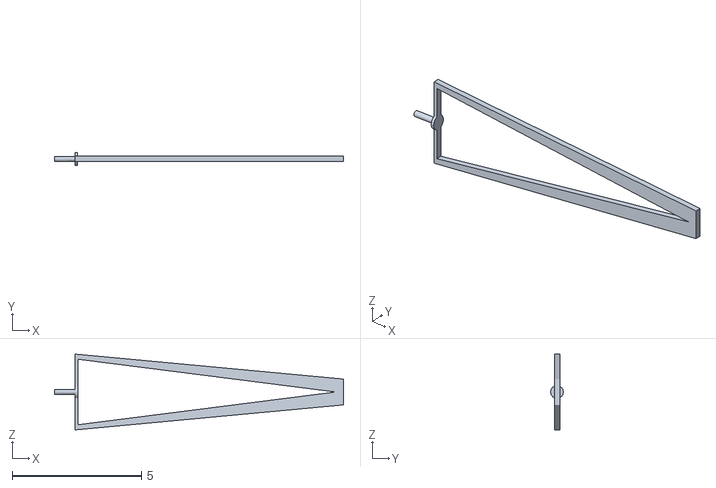
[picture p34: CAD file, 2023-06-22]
whisker_deflectors/piezo_mounted_whisk_deflector_LONG.stl
11.2 x 0.5 x 2.94

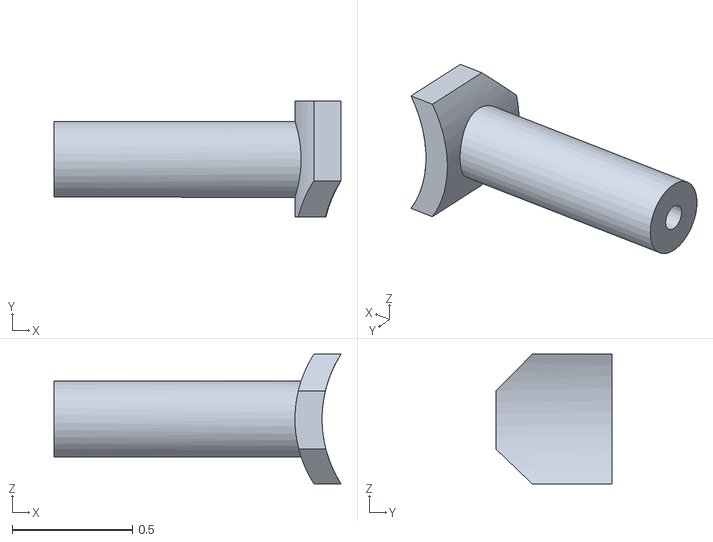
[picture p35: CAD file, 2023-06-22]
window_stabilizers/10mm_radius_labmaker_cSkull_mold_window_stabilizer.stl
1.19 x 0.483 x 0.538

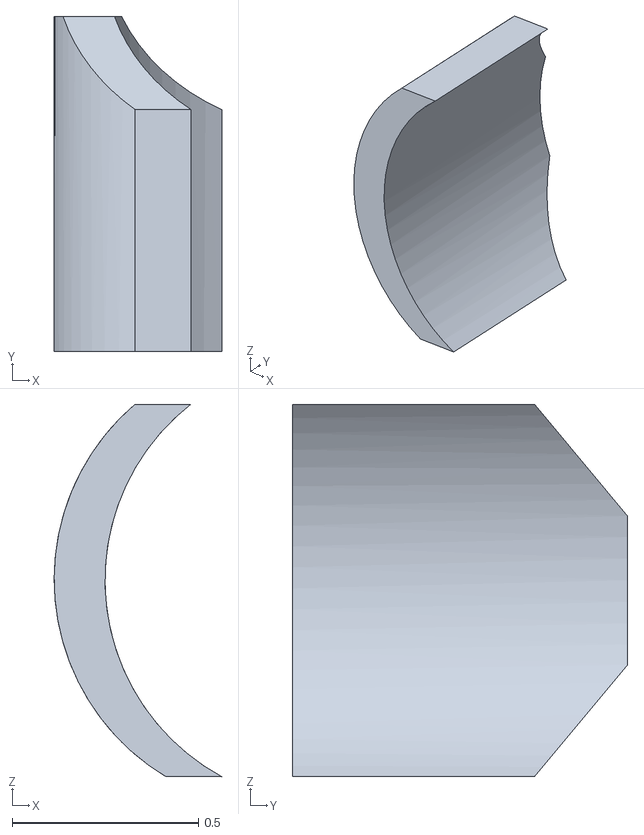
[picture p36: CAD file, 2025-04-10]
cranial_windows/dorsal_mount/12mm_radius_mold_with_crystal_skull_thick.stl
0.45 x 0.899 x 1

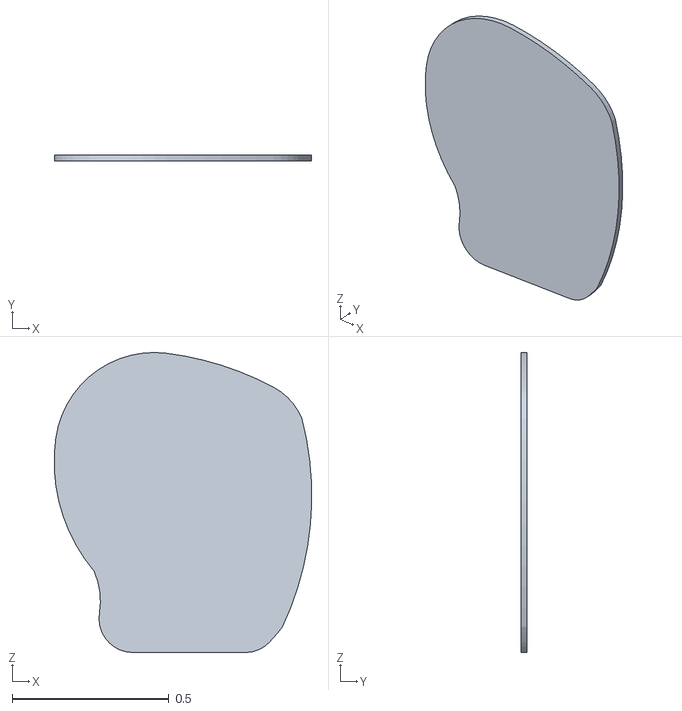
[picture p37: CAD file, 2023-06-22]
cranial_windows/side_mount/side_mount_large_10_mm_radius_3D_v1.stl
0.822 x 0.02 x 0.958

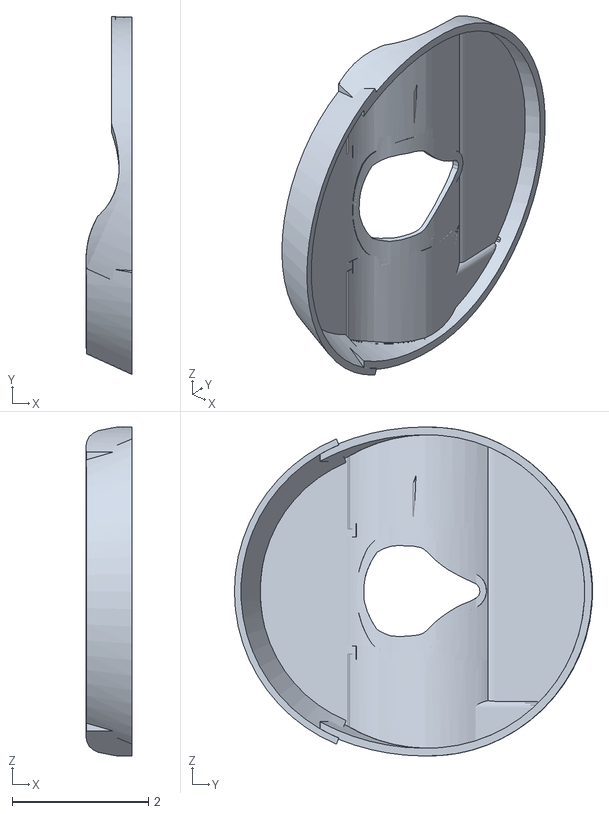
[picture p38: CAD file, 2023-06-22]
dorsal_mount_woks/dorsal_mount_wok1_alt.stl
0.679 x 5.26 x 4.83

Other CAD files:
headposts/side_mount/side_mount_headpost.stl
headposts/dorsal_mount/dorsal_mount_small.stp
side_mount_woks/side_mount_wok1_tall_rim_sculpted_alt.stl
support_arms/left_support_arm.stl
cranial_windows/dorsal_mount/10mm_radius_mold.ipt
cranial_windows/dorsal_mount/10mm_radius_mold.stl
cranial_windows/dorsal_mount/11mm_radius_mold.ipt
cranial_windows/dorsal_mount/11mm_radius_mold.stl
cranial_windows/dorsal_mount/12mm_radius_mold.ipt
cranial_windows/dorsal_mount/12mm_radius_mold.stl
cranial_windows/dorsal_mount/12mm_radius_mold_with_crystal_skull.ipt
cranial_windows/dorsal_mount/12mm_radius_mold_with_crystal_skull.stl
cranial_windows/dorsal_mount/13mm_radius_mold_with_crystal_skull.ipt
cranial_windows/dorsal_mount/14mm_radius_mold_with_crystal_skull.ipt
cranial_windows/dorsal_mount/14mm_radius_mold_with_crystal_skull.stl
cranial_windows/dorsal_mount/15mm_radius_mold_with_crystal_skull.ipt
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

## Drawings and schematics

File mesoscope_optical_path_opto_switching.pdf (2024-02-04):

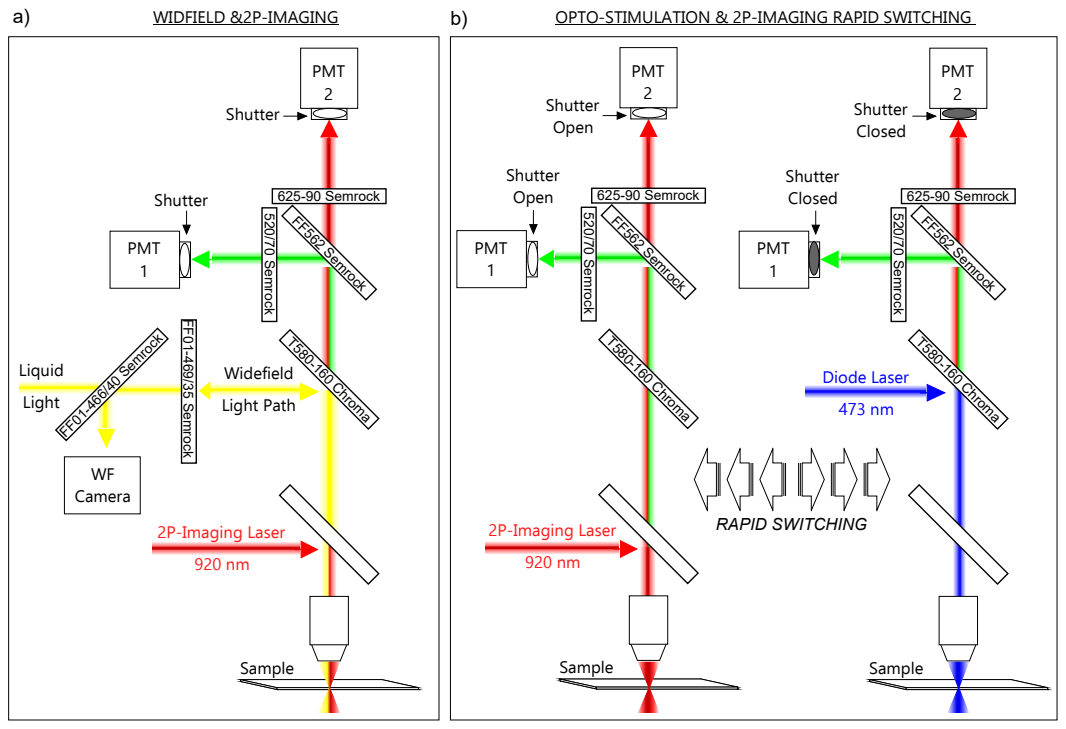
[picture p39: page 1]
PMT 2; Widefield Light Path; T580-160 Chroma; FF562 Semrock; 0 S e mro; PMT 1; 625-90 Semrock; Sample; 2P-Imaging Laser 920 nm; Shutter; WF Camera; FF01-466/40 Semrock; 5 S e mro; Shutter Open; Diode Laser 473 nm; Shutter Closed; RAPID SWITCHING; Liquid Light; WIDFIELD &2P-IMAGING; OPTO-STIMULATION & 2P-IMAGING RAPID SWITCHING

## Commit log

2023-06-09 Dorsal and side mount headposts, 3D pdfs
    3D printed in titanium
2023-10-23 Add files via upload
    A provisional patent application (UOR-145-PROV) was filed for this process and device on October 20th, 2023. -Evan Vickers
